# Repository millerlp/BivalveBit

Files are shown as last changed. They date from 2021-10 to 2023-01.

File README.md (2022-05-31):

# BivalveBit

A custom data logger designed to monitor bivalve mollusc heart rate, valve
gape, and external temperature. Designed to be housed in a 3/4" schedule 40 
PVC plumbing pipe along with an 18650-size Lithium-Ion battery cell. 

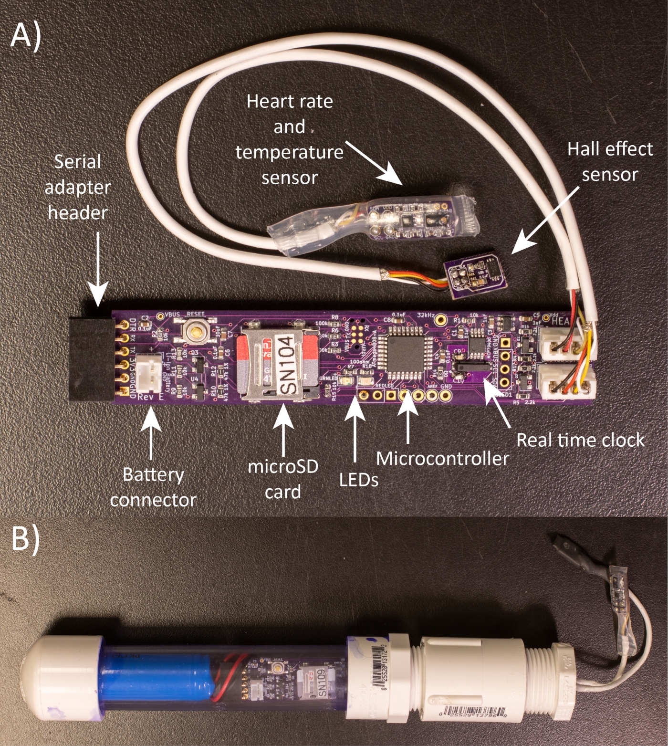
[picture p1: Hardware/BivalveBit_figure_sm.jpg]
Revision E circuit board


Current hardware revision E (Fall 2021). See the Hardware folder for KiCad
design files.

Programmed in the Arduino environment.
 
Requires the separate BivalveBit_lib library available at: 
https://github.com/millerlp/BivalveBit_lib

 Based on ATmega4808 MCU using MegaCoreX board definition
 https://github.com/MCUdude/MegaCoreX

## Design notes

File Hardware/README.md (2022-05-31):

# BivalveBit hardware
 Heart rate and valve gape sensor wearable for oysters and mussels. 
 
 * Based around a ATmega4808 microcontroller
 * Designed to fit inside a nominal 3/4" schedule 40 PVC plumbing pipe (<18.5mm
 inside diameter) along with an 18650 size Lithium-Ion battery cell. 
 * Provides one I2C 4-pin port for communicating with a IR heart rate sensor
 * Provides one analog 4-pin port for communicating with an analog sensor such
 as the A1395 Hall effect sensor (with SLEEP pin on the 4th wire). 
 * Writes data to a standard microSD card
 
 Hardware design files for the main board were originally created in KiCad 5.1, 
 in the directory BivalveBit_RevE. The files have been updated to KiCad 6.0.1. 
 
 Hardware design files for the heart rate (and temperature) sensor board
 were created in Autodesk EAGLE 9.6, and are available in the 
 Mussel_heartrate_RevC_EAGLE directory. A version imported into KiCad 6.0.1 is available
 in the directory Mussel_heartrate_RevC_KiCad. 
 
 Hardware design files in KiCad 6.0.1 for the Hall effect sensor board using an Allegro A1395
 Hall effect sensor can be found in the directory Hall_effect_sensor_board_A139x.

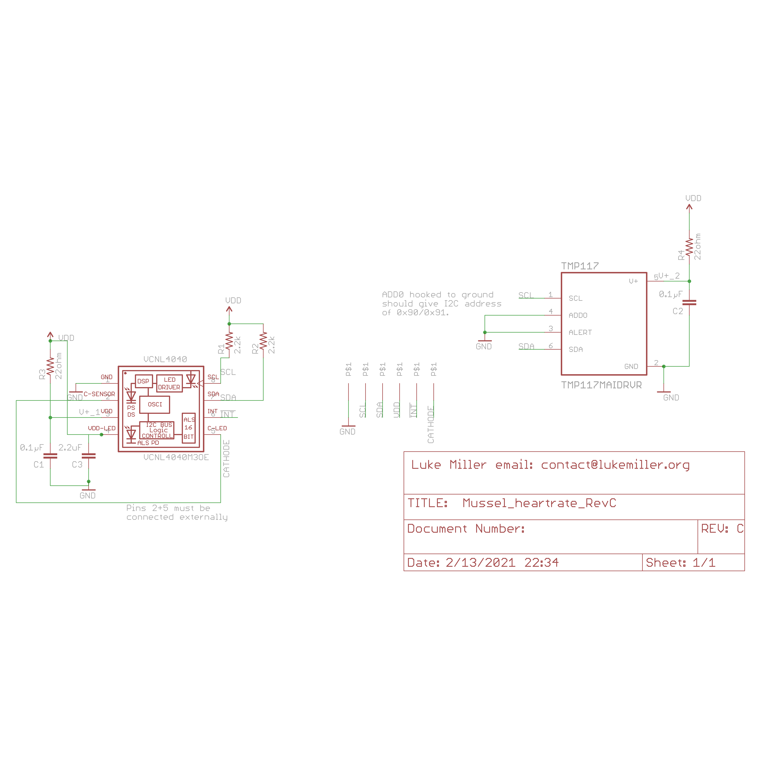
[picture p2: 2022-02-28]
Hardware/Mussel_heartrate_RevC_EAGLE/Mussel_heartrate_RevC_schematic.png

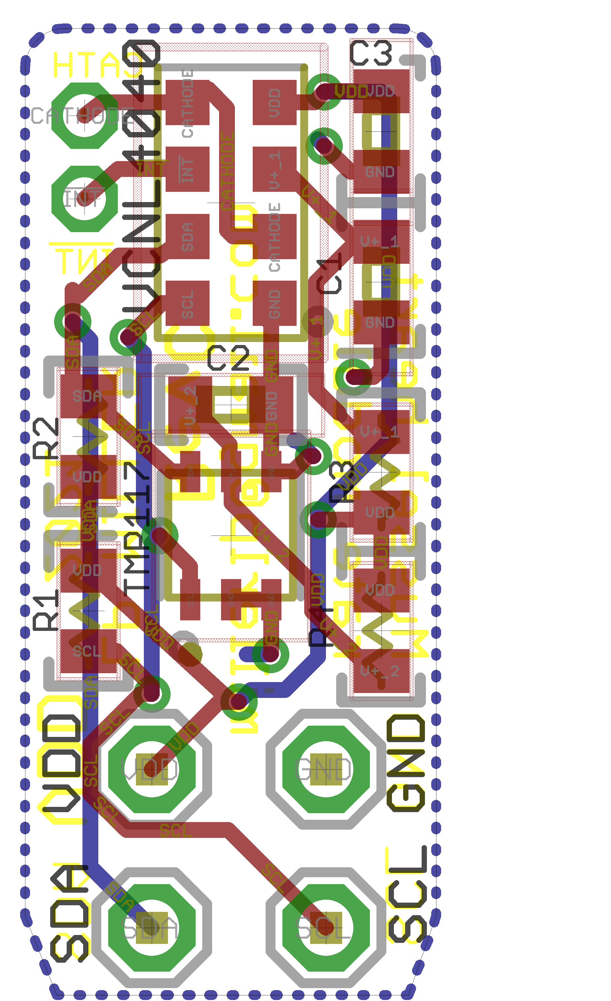
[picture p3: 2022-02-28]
Hardware/Mussel_heartrate_RevC_EAGLE/Mussel_heartrate_RevC_board.png

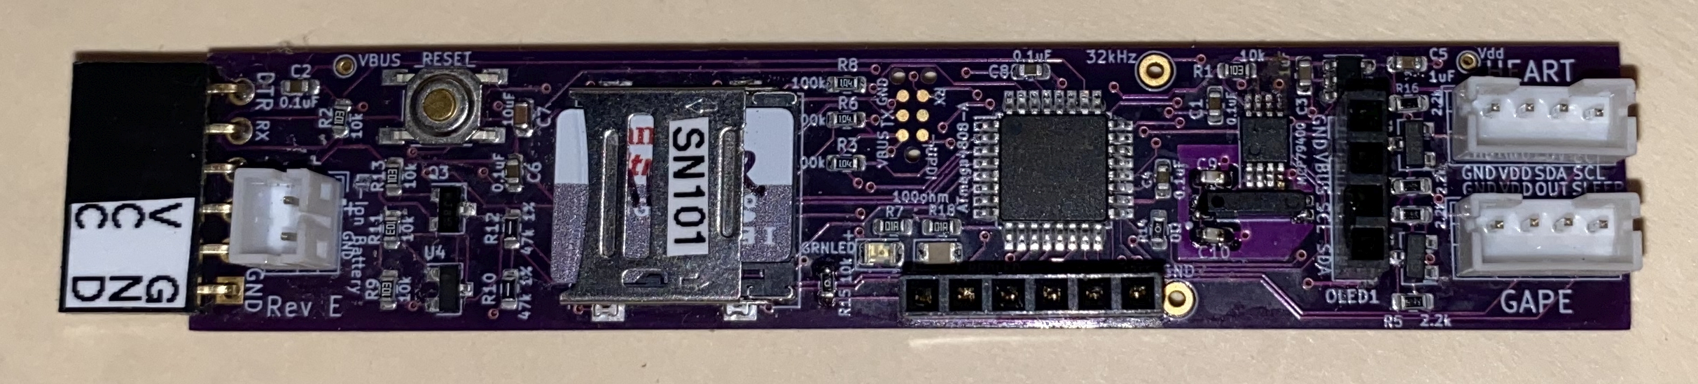
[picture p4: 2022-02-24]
Hardware/BivalveBit_RevE/BivalveBit_RevE_board.jpg

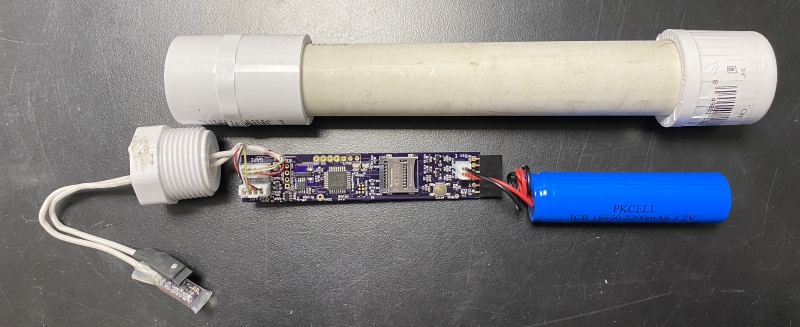
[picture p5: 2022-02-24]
Hardware/BivalveBit_RevE_hardware.jpg

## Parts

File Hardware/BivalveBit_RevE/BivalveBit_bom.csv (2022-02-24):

Id | Designator | Package | Quantity | Designation | Supplier and ref
1 | TP2,TP1 | TestPoint_THTPad_D1.0mm_Drill0.5mm | 2 | TestPoint_Probe
2 | RTC_BATT1 | BatteryHolder_Keystone_3000_1x12mm | 1 | Battery_Cell
3 | JP2,JP1 | SolderJumper-3_P1.3mm_Bridged12_RoundedPad1.0x1.5mm | 2 | SolderJumper_3_Bridged12
4 | HEART_SENSOR1,HALL_SENSOR1 | JST_PH_B4B-PH-K_1x04_P2.00mm_Vertical | 2 | Conn_01x04_Male
5 | R17,R16,R5,R4 | R_0603_1608Metric | 4 | 2.2k
6 | U4 | SOT-23 | 1 | BJT_NPN
7 | U3 | SOT-23-5 | 1 | LP5907MFX-3.0
8 | U2 | TQFP-32_7x7mm_P0.8mm | 1 | ATmega4808-A
9 | SW2 | SW_SPST_REED_CT10-XXXX-G1 | 1 | SW_Reed
10 | RESET1 | SW_PTS525SM15SMTR2LFS | 1 | PTS525SM15SMTR2LFS
11 | R15,R13,R11,R9,R2,R1 | R_0603_1608Metric | 6 | 10k
12 | R14 | R_0603_1608Metric | 1 | 0Ω
13 | R12,R10 | R_0603_1608Metric | 2 | 47k 1%
14 | R8,R6,R3 | R_0603_1608Metric | 3 | 100k
15 | R7,R18 | R_0603_1608Metric | 2 | 100ohm
16 | Q3 | SOT-23 | 1 | P-FET
17 | Q2,Q1 | SOT-23 | 2 | BSS138
18 | PROGRAM_HEADER1 | Tag-Connect_TC2030-IDC-NL_2x03_P1.27mm_Vertical | 1 | TC2030-IDC-NL-UPDI
19 | PRIMARY_BATTERY1 | JST_PH_B2B-PH-K_1x02_P2.00mm_Vertical | 1 | Conn_01x02
20 | OLED1 | PinHeader_1x04_P2.54mm_Vertical | 1 | Conn_01x04
21 | microSD1 | MOLEX_47219-2001 | 1 | 47219-2001
22 | J7,J5,J4,J8,J2 | Pin_D1.0mm_L10.0mm | 5 | Conn_01x01_Male
23 | J6 | PinHeader_1x03_P2.54mm_Vertical | 1 | Conn_01x03_Male
24 | FTDI1 | PinSocket_1x06_P2.54mm_Horizontal | 1 | Conn_01x06
25 | D1 | LED_0805_2012Metric | 1 | GRNLED
26 | Crystal_32.768kHz1 | OSC_SSP-T7-F | 1 | SSP-T7-F
27 | C8,C6,C4,C2,C1 | C_0603_1608Metric | 5 | 0.1uF
28 | C7 | C_0603_1608Metric | 1 | 10uF
29 | C5,C3 | C_0603_1608Metric | 2 | 1uF
30 | C9,C10 | C_0603_1608Metric | 2 | 4-16pF
31 | RTC1 | MSOP-8_3x3mm_P0.65mm | 1 | MCP79400
32 | D2 | LED_0805_2012Metric | 1 | REDLED

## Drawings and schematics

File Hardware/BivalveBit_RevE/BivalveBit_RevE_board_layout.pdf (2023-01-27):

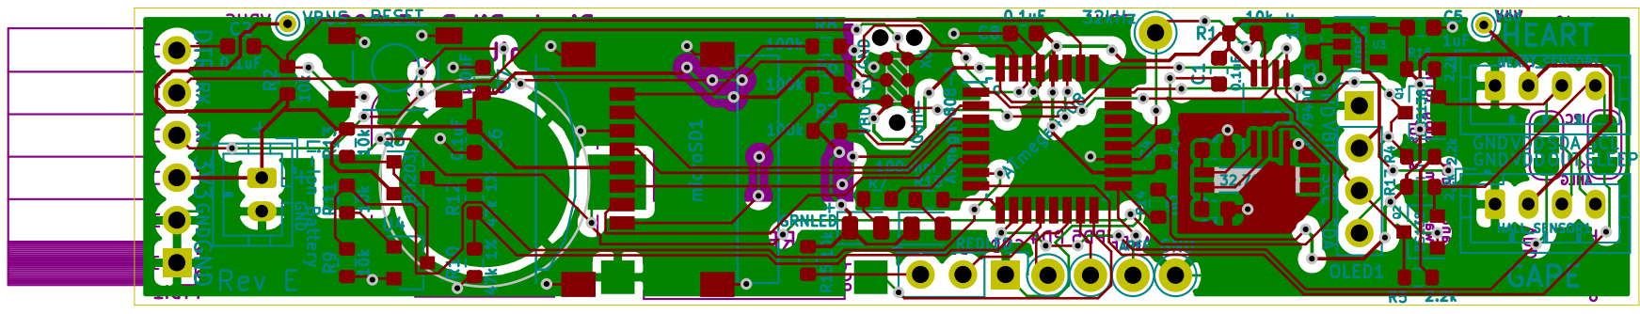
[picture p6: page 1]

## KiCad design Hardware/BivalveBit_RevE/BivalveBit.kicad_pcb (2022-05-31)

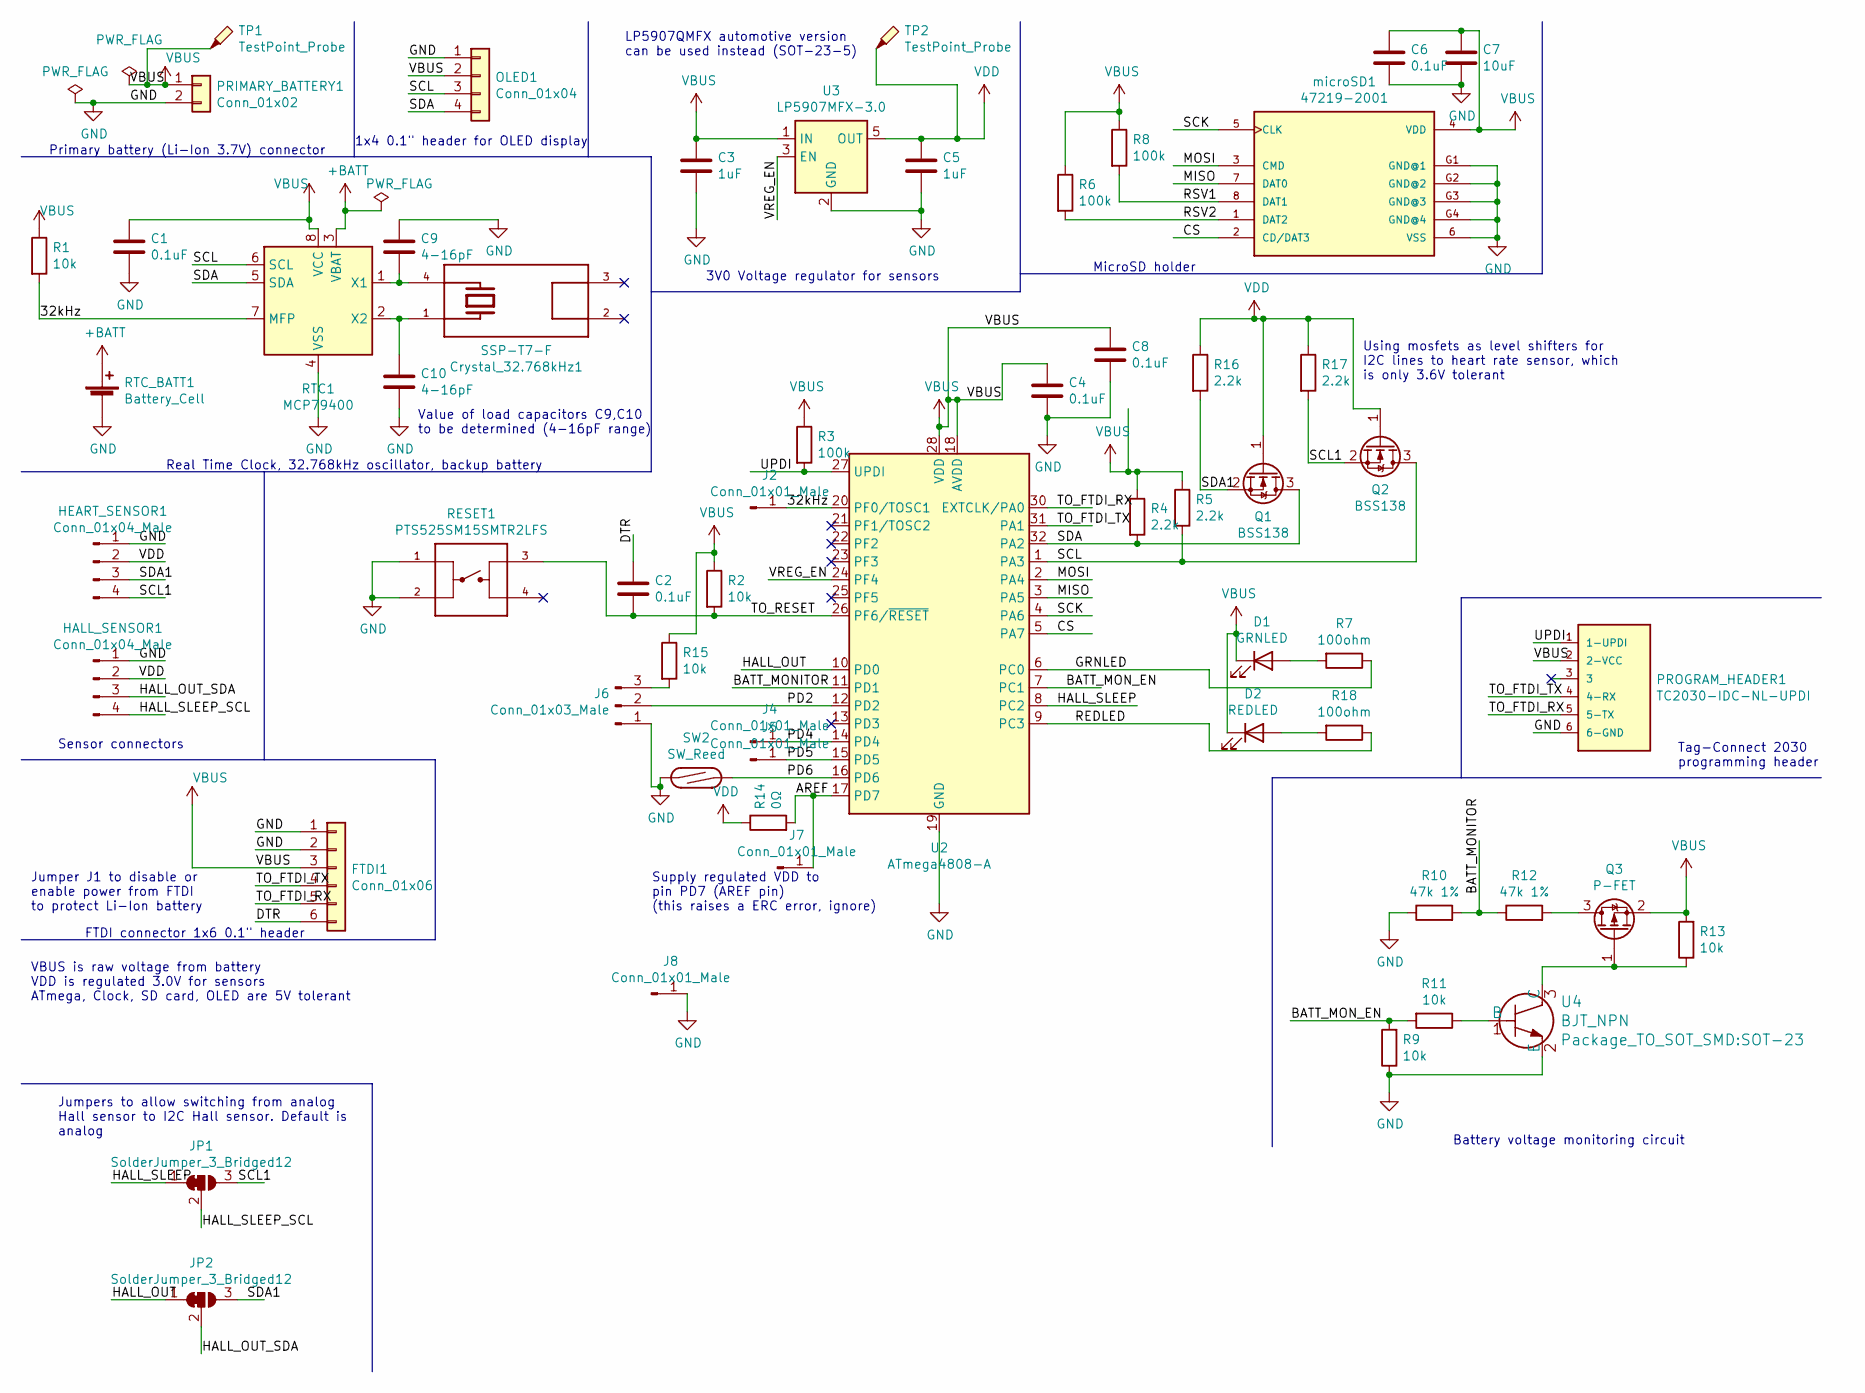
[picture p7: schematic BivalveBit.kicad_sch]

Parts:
C1, C2, C4, C6, C8: 0.1uF; C_0603_1608Metric
C3, C5: 1uF; C_0603_1608Metric
C7: 10uF; C_0603_1608Metric
C9, C10: 4-16pF; C_0603_1608Metric
Crystal_32.768kHz1: SSP-T7-F; OSC_SSP-T7-F; PARTREV N/A
D1: GRNLED; LED_0805_2012Metric
D2: REDLED; LED_0805_2012Metric
FTDI1: Conn_01x06; PinSocket_1x06_P2.54mm_Horizontal
HALL_SENSOR1: Conn_01x04_Male; JST_PH_B4B-PH-K_1x04_P2.00mm_Vertical
HEART_SENSOR1: Conn_01x04_Male; JST_PH_B4B-PH-K_1x04_P2.00mm_Vertical
J2, J4, J5, J7, J8: Conn_01x01_Male; Pin_D1.0mm_L10.0mm
J6: Conn_01x03_Male; PinHeader_1x03_P2.54mm_Vertical
JP1, JP2: SolderJumper_3_Bridged12; SolderJumper-3_P1.3mm_Bridged12_RoundedPad1.0x1.5mm
OLED1: Conn_01x04; PinHeader_1x04_P2.54mm_Vertical
PRIMARY_BATTERY1: Conn_01x02; JST_PH_B2B-PH-K_1x02_P2.00mm_Vertical
PROGRAM_HEADER1: TC2030-IDC-NL-UPDI; Tag-Connect_TC2030-IDC-NL_2x03_P1.27mm_Vertical; PARTREV MS
Q1, Q2: BSS138; SOT-23
Q3: P-FET; SOT-23
R1, R2, R9, R11, R13, R15: 10k; R_0603_1608Metric
R3, R6, R8: 100k; R_0603_1608Metric
R4, R5, R16, R17: 2.2k; R_0603_1608Metric
R7, R18: 100ohm; R_0603_1608Metric
R10, R12: 47k 1%; R_0603_1608Metric
R14: 0Ω; R_0603_1608Metric
RESET1: PTS525SM15SMTR2LFS; SW_PTS525SM15SMTR2LFS; PARTREV NA
RTC1: MCP79400; MSOP-8_3x3mm_P0.65mm
RTC_BATT1: Battery_Cell; BatteryHolder_Keystone_3000_1x12mm
SW2: SW_Reed; SW_SPST_REED_CT10-XXXX-G1
TP1, TP2: TestPoint_Probe; TestPoint_THTPad_D1.0mm_Drill0.5mm
U2: ATmega4808-A; TQFP-32_7x7mm_P0.8mm
U3: LP5907MFX-3.0; SOT-23-5
U4: BJT_NPN; SOT-23
microSD1: 47219-2001; MOLEX_47219-2001; Digikey WM6698CT-ND

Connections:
+BATT: RTC1.3 (VBAT), RTC_BATT1.1 (+)
/32kHz: J2.1, R1.2, RTC1.7 (MFP), U2.20 (PF0/TOSC1)
/AREF: J7.1, R14.2, U2.17 (PD7)
/BATT_MONITOR: R10.2, R12.1, U2.11 (PD1)
/BATT_MON_EN: R9.2, R11.2, U2.7 (PC1)
/CS: U2.5 (PA7), microSD1.2 (CD/DAT3)
/DTR: C2.1, FTDI1.6
/GRNLED: R7.1, U2.6 (PC0)
/HALL_OUT: JP2.1 (A), U2.10 (PD0)
/HALL_OUT_SDA: HALL_SENSOR1.3, JP2.2 (C)
/HALL_SLEEP: JP1.1 (A), U2.8 (PC2)
/HALL_SLEEP_SCL: HALL_SENSOR1.4, JP1.2 (C)
/MISO: U2.3 (PA5), microSD1.7 (DAT0)
/MOSI: U2.2 (PA4), microSD1.3 (CMD)
/PD2: J6.2, U2.12 (PD2)
/PD4: J4.1, U2.14 (PD4)
/PD5: J5.1, U2.15 (PD5)
/PD6: SW2.2, U2.16 (PD6)
/REDLED: R18.1, U2.9 (PC3)
/RSV1: R8.2, microSD1.8 (DAT1)
/RSV2: R6.2, microSD1.1 (DAT2)
/SCK: U2.4 (PA6), microSD1.5 (CLK)
/SCL: OLED1.3, Q2.3 (D), R5.2, RTC1.6 (SCL), U2.1 (PA3)
/SCL1: HEART_SENSOR1.4, JP1.3 (B), Q2.2 (S), R17.2
/SDA: OLED1.4, Q1.3 (D), R4.2, RTC1.5 (SDA), U2.32 (PA2)
/SDA1: HEART_SENSOR1.3, JP2.3 (B), Q1.2 (S), R16.2
/TO_FTDI_RX: FTDI1.5, PROGRAM_HEADER1.5 (5-TX), U2.30 (EXTCLK/PA0)
/TO_FTDI_TX: FTDI1.4, PROGRAM_HEADER1.4 (4-RX), U2.31 (PA1)
/TO_RESET: C2.2, R2.2, RESET1.3, U2.26 (PF6/~RESET)
/UPDI: PROGRAM_HEADER1.1 (1-UPDI), R3.2, U2.27 (UPDI)
/VREG_EN: U2.24 (PF4), U3.3 (EN)
GND: C1.2, C3.2, C4.2, C5.2, C6.2, C7.2, C8.2, C9.1, C10.2, FTDI1.1, FTDI1.2, HALL_SENSOR1.1, HEART_SENSOR1.1, J6.1, J8.1, OLED1.1, PRIMARY_BATTERY1.2, PROGRAM_HEADER1.6 (6-GND), R9.1, R10.1, RESET1.1, RESET1.2, RTC1.4 (VSS), RTC_BATT1.2 (-), SW2.1, U2.19 (GND), U2.29 (GND), U3.2 (GND), U4.2 (E), microSD1.6 (VSS), microSD1.G1 (GND@1), microSD1.G2 (GND@2), microSD1.G3 (GND@3), microSD1.G4 (GND@4)
unnamed: C9.2, Crystal_32.768kHz1.4, RTC1.1 (X1)
unnamed: C10.1, Crystal_32.768kHz1.1, RTC1.2 (X2)
unnamed: D1.2 (A), R7.2
unnamed: D2.2 (A), R18.2
unnamed: J6.3, R15.2
unnamed: Q3.1 (G), R13.1, U4.3 (C)
unnamed: Q3.3 (D), R12.2
unnamed: R11.1, U4.1 (B)
VBUS: C1.1, C3.1, C4.1, C6.1, C7.1, C8.1, D1.1 (K), D2.1 (K), FTDI1.3, OLED1.2, PRIMARY_BATTERY1.1, PROGRAM_HEADER1.2 (2-VCC), Q3.2 (S), R1.1, R2.1, R3.1, R4.1, R5.1, R6.1, R8.1, R13.2, R15.1, RTC1.8 (VCC), TP1.1, U2.18 (AVDD), U2.28 (VDD), U3.1 (IN), microSD1.4 (VDD)
VDD: C5.1, HALL_SENSOR1.2, HEART_SENSOR1.2, Q1.1 (G), Q2.1 (G), R14.1, R16.1, R17.1, TP2.1, U3.5 (OUT)

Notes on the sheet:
Primary battery (Li-Ion 3.7V) connector
Battery voltage monitoring circuit
Using mosfets as level shifters for I2C lines to heart rate sensor, which is only 3.6V tolerant
Jumpers to allow switching from analog Hall sensor to I2C Hall sensor. Default is analog
FTDI connector 1x6 0.1" header
Sensor connectors
1x4 0.1" header for OLED display
Real Time Clock, 32.768kHz oscillator, backup battery
Supply regulated VDD to pin PD7 (AREF pin) (this raises a ERC error, ignore)
Value of load capacitors C9,C10 to be determined (4-16pF range)
LP5907QMFX automotive version can be used instead (SOT-23-5)
Jumper J1 to disable or enable power from FTDI to protect Li-Ion battery
3V0 Voltage regulator for sensors
VBUS is raw voltage from battery VDD is regulated 3.0V for sensors ATmega, Clock, SD card, OLED are 5V tolerant
MicroSD holder
Tag-Connect 2030 programming header

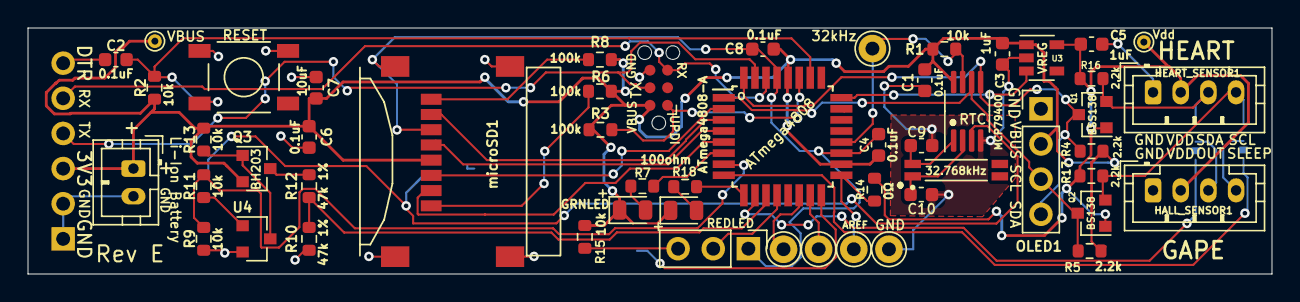
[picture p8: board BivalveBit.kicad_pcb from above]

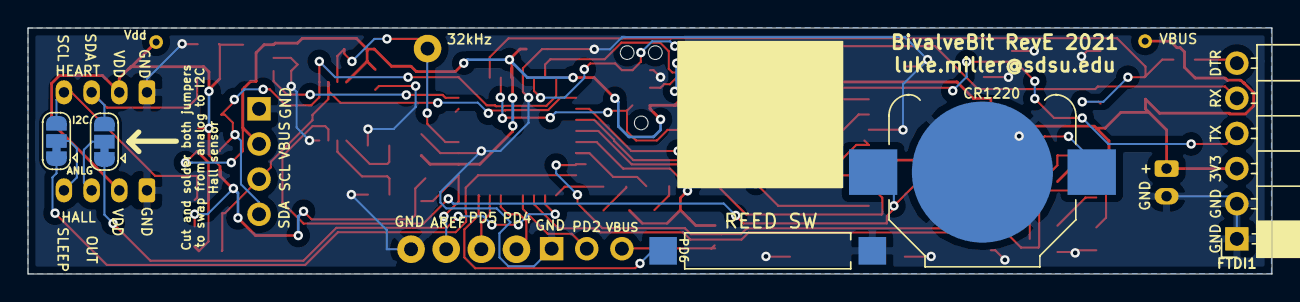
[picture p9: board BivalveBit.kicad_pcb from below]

Board: 2 copper layers, 89.9 x 17.8 mm, 58 parts (5 on the bottom side), 42 nets.

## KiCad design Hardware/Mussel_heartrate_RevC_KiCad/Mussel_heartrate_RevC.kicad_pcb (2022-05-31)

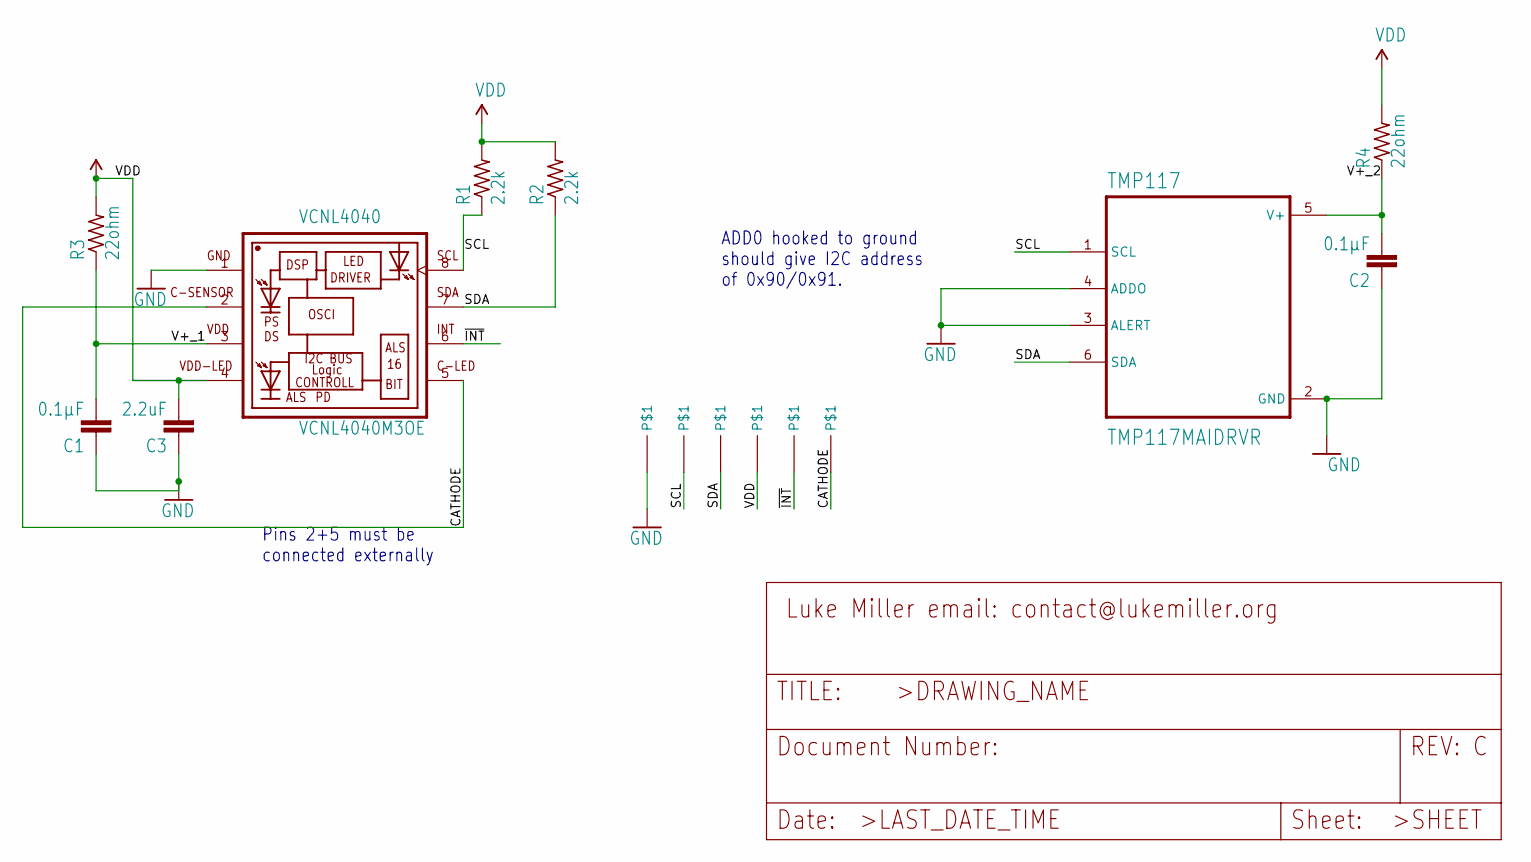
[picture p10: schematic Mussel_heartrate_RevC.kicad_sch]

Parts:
/~{INT}1: PINHD-1X10.7MM_DRILL; 1X01_SMALL_0.7
C1, C2: 0.1µF; C0402
C3: 2.2uF; C0402
CATHODE1: PINHD-1X10.7MM_DRILL; 1X01_SMALL_0.7
GND1: PINHD-1X1SMALL; 1X01_SMALL_HEADER_PIN_D0.9MM_W1.4MM
R1, R2: 2.2k; R0402
R3, R4: 22ohm; R0402
SCL1: PINHD-1X1SMALL; 1X01_SMALL_HEADER_PIN_D0.9MM_W1.4MM
SDA1: PINHD-1X1SMALL; 1X01_SMALL_HEADER_PIN_D0.9MM_W1.4MM
TMP117: TMP117MAIDRVR; SON65P200X200X80-7N
VCNL4040: VCNL4040M3OE; VISHAY_VCNL4040_4X2X1.1
VDD1: PINHD-1X1SMALL; 1X01_SMALL_HEADER_PIN_D0.9MM_W1.4MM

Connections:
/CATHODE: CATHODE1.P$1, VCNL4040.2 (C-SENSOR), VCNL4040.5 (C-LED)
/SCL: R1.1, SCL1.1, TMP117.1 (SCL), VCNL4040.8 (SCL)
/SDA: R2.1, SDA1.1, TMP117.6 (SDA), VCNL4040.7 (SDA)
/V+_1: C1.2, R3.1, VCNL4040.3 (VDD)
/V+_2: C2.2, R4.1, TMP117.5 (V+)
/~INT: /~{INT}1.P$1, VCNL4040.6 (INT)
GND: C1.1, C2.1, C3.1, GND1.1, TMP117.2 (GND), TMP117.3 (ALERT), TMP117.4 (ADDO), VCNL4040.1 (GND)
VCC: C3.2, R1.2, R2.2, R3.2, R4.2, VCNL4040.4 (VDD-LED), VDD1.1

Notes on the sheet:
ADD0 hooked to ground should give I2C address of 0x90/0x91.
Pins 2+5 must be connected externally

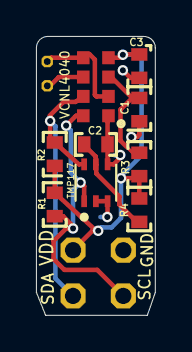
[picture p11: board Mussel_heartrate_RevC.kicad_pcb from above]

Board: 2 copper layers, 6.6 x 15.5 mm, 15 parts (0 on the bottom side), 8 nets.

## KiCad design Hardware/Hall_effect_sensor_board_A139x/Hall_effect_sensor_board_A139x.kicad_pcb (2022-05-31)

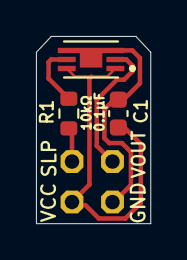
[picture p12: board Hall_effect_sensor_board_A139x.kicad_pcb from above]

Board: 2 copper layers, 6.4 x 10.4 mm, 4 parts (0 on the bottom side), 5 nets.

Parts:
C1: 0.1µF; C_0603_1608Metric
HALL1_HEADER1: PINHD-2X21.5MM_SILK; 2X2_2.25MM
R1: 10kΩ; R_0603_1608Metric
U1: A1395SEHLT-T; SENSOR_A1395SEHLT-T

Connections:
/HALL1_GND: C1.2, HALL1_HEADER1.P$1 (1), U1.3 (GND), U1.4 (GND)
/HALL1_VCC: C1.1, HALL1_HEADER1.P$2 (2), U1.1 (VCC), U1.6 (VREF)
/HALL1_VOUT: HALL1_HEADER1.P$3 (3), U1.2 (OUT)
/HALL1_~SLEEP_IN: HALL1_HEADER1.P$4 (4), R1.1
/~SLEEP1: R1.2, U1.5 (~SLEEP)

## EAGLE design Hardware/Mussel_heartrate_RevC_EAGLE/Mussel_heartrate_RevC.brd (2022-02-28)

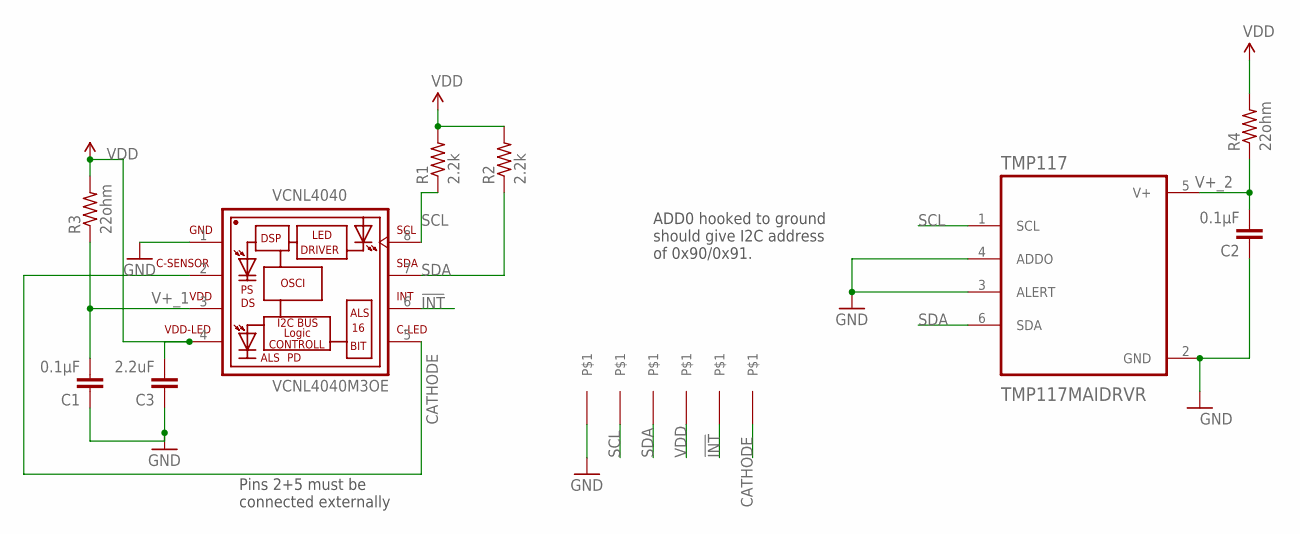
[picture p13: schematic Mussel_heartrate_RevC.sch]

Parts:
!INT, !INT1: PINHD-1X10.7MM_DRILL; 1X01_SMALL_0.7
C1, C2: 0.1µF; C0402
C3: 2.2uF; C0402
GND: PINHD-1X1SMALL; 1X01_SMALL
R1, R2: 2.2k; R0402
R3, R4: 22ohm; R0402
SCL: PINHD-1X1SMALL; 1X01_SMALL
SDA: PINHD-1X1SMALL; 1X01_SMALL
TMP117: TMP117MAIDRVR; SON65P200X200X80-7N
VCNL4040: VCNL4040M3OE; VISHAY_VCNL4040_4X2X1.1
VDD: PINHD-1X1SMALL; 1X01_SMALL

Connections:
!INT: !INT.P$1, VCNL4040.6 (INT)
CATHODE: !INT1.P$1, VCNL4040.2 (C-SENSOR), VCNL4040.5 (C-LED)
GND: C1.1, C2.1, C3.1, GND.1, TMP117.2 (GND), TMP117.3 (ALERT), TMP117.4 (ADDO), VCNL4040.1 (GND)
SCL: R1.1, SCL.1, TMP117.1 (SCL), VCNL4040.8 (SCL)
SDA: R2.1, SDA.1, TMP117.6 (SDA), VCNL4040.7 (SDA)
V+_1: C1.2, R3.1, VCNL4040.3 (VDD)
V+_2: C2.2, R4.1, TMP117.5 (V+)
VDD: C3.2, R1.2, R2.2, R3.2, R4.2, VCNL4040.4 (VDD-LED), VDD.1

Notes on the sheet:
ADD0 hooked to ground should give I2C address of 0x90/0x91.
Pins 2+5 must be connected externally

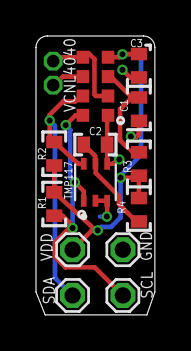
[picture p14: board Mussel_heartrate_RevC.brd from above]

Board: 2 copper layers, 6.6 x 15.5 mm, 15 parts (0 on the bottom side), 8 nets.

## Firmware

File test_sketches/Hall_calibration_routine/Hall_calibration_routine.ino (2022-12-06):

/* Hall_calibration_routine.ino
 *  BivalveBit data logger program to calibration Hall effect sensor
 *  of a KD Scientific Model 200 syringe dispenser.
 *  
 *  Compile with MegaCoreX: ATmega4808, 32 pin, BOD 2.6V, Internal 8MHz, Optiboot (UART0 default pins)
 *  

 *  Meant to work with a BivalveBit board. Connect
 *  to a KD Scientific Model 200 syringe dispenser to move the 
 *  dispenser a known distances, causing the 
 *  magnetic field of a Hall effect sensor to change in response.
 *  If you don't have a Model 200 syringe dispenser sitting around,
 *  don't bother running this program.
 *  
 *  Connect Syringe Trigger pin to MusselTracker pin PD2
 *  Connect Syringe GND to MusselTracker GND
 *  On the KD200 dispenser, set the syringe DIA to 50.00mm
 *  Set the Vol to 0.623ml
 *  Set the Rate to 40 ml/m
 *  
 *  To start a calibration run, open the Serial Monitor and type CALIB and 
 *  hit return. The program will step the syringe pump through the various 
 *  distances, with the first distance marked as "0.0" mm. It will stop after 
 *  moving about 12mm, at which point you can release the carriage and return
 *  it to a starting point. Another run can be started by typing CALIB again,
 *  and the new run will written into the same file as the previous run. 
 *  
 *  If the device just slowly flashes red after startup, the real time clock
 *  needs to be reset. Open the serial monitor and enter the correct date and
 *  time (in the UTC time zone preferably) using the command format:
 *  SETDATE YYYY-MM-DD HH:MM:SS
 *  
 */


#include "SdFat.h" // https://github.com/greiman/SdFat (you must be using ver. 2.1.2 or higher)
#include <Wire.h>  // built in library, for I2C communications
#include <EEPROM.h>
#include <avr/io.h>
#include <avr/interrupt.h>
#include <avr/sleep.h>
#include <avr/cpufunc.h>
//#include "SSD1306Ascii.h" // https://github.com/greiman/SSD1306Ascii
//#include "SSD1306AsciiWire.h" // https://github.com/greiman/SSD1306Ascii
#include "MCP7940.h"  // https://github.com/Zanduino/MCP7940  Real time clock
//#include "Adafruit_VCNL4040.h" // https://github.com/adafruit/Adafruit_VCNL4040 & https://github.com/adafruit/Adafruit_BusIO
//#include "SparkFun_TMP117.h" // https://github.com/sparkfun/SparkFun_TMP117_Arduino_Library
#include "BivalveBit_lib.h" // https://github.com/millerlp/BivalveBit_lib


//*************************************
float moveDist = 0.3175; // units mm, if pump set to dispense 0.1mL
float moveLimit = 12.5; // units millimeters
float distanceVal = 0; // keep track of distance moved
uint8_t TrialNum = 0;   // Trial number counter
//*************

// -------------------------------------------
// ***** STATE MACHINE TYPE DEFINITIONS *****
typedef enum STATE
{
  STATE_IDLE,         // Idle and wait for user input
  STATE_CALIB     // Go into Hall effect calibration mode
} mainState_t;
// main state machine variable, this takes on the various
// values defined for the STATE typedef above. 
mainState_t mainState;

// Type definition for a case structure to write to SD card or skip writing
typedef enum WRITE_SD
{
  WRITE_HALL_TEMP_VOLTS, // collect Hall sensor data and battery voltage data
  WRITE_HEART, // collect heart rate data at sub-second intervals
  WRITE_NOTHING // don't write anything
  
} writeState_t;
writeState_t writeState;

/*******************************************************
 * SD card objects
 *******************************************************/
// SPI pins for SD card
const uint8_t SD_CHIP_SELECT = 7;
#define MOSI 4
#define MISO 5
#define SCK 6
SdFat sd; 
SdFile GAPEFile; //SD card object
bool SDfailFlag = false;
// Placeholder serialNumber
char serialNumber[] = "SN000";
bool serialValid = false;
// Declare initial name for output files written to SD card
char gapefilename[] =   "SN000_YYYYMMDD_HHMM_CALIB.csv";

/************************************************************
 * Hall effect sensor definitions
 ************************************************************/
#define ANALOG_IN A0  // Analog input pin for Hall sensor
#define HALL_SLEEP 10 // Hall sensor sleep pin, pull high to wake
unsigned int HallValue = 0; // Variable for Hall sensor reading

/***************************************************************************************************
** Declare global variables and instantiate classes for MCP79400 real time clock                                              
*   This library is written for the MCP7940, but works with the BivalveBit MCP79400
***************************************************************************************************/
MCP7940_Class MCP7940;                           // Create an instance of the MCP7940

const uint32_t SERIAL_SPEED{57600};     // Set the baud rate for Serial I/O
const uint8_t  SPRINTF_BUFFER_SIZE{32};  // Buffer size for sprintf()
char          inputBuffer[SPRINTF_BUFFER_SIZE];  // Buffer for sprintf()/sscanf()
DateTime now; // Variable to hold current time
DateTime firsttimestamp; // Variable to track fast sampling start 
DateTime lasttimestamp; // Variable to track fast sampling end time
byte oldday1; // Used to track midnight change
byte oldday2; // Used to track midnight change
/*! ///< Enumeration of MCP7940 alarm types */
enum alarmTypes {
  matchSeconds,
  matchMinutes,
  matchHours,
  matchDayOfWeek,
  matchDayOfMonth,
  Unused1,
  Unused2,
  matchAll,
  Unknown
};

//------------------------------------------------------------
//  Battery monitor 
#define BATT_MONITOR_EN  9 // digital output channel to turn on battery voltage check
#define BATT_MONITOR  A1  // analog input channel to sense battery voltage
float dividerRatio = 2; // Ratio of voltage divider (47k + 47k) / 47k = 2
float refVoltage = 3.00; // Voltage at AREF pin on ATmega microcontroller, measured per board
float batteryVolts = 0; // Estimated battery voltage returned from readBatteryVoltage function
float minimumVoltage = 3.4; // Minimum safe voltage for a Li-Ion battery
unsigned int lowVoltageCount = 0; // Count how many times voltage is too low
unsigned int lowVoltageCountLimit = 10; // Number of loops after which the program should be shutdown
#define REDLED 11   // Red LED pin
#define GRNLED 8    // Green LED pin
#define VREG_EN 24  // voltage regulator enable
#define TRIGGER 14 // External trigger to syringe pump, PD2 pin, Arduino pin 14(A2)


void test_pin_init(void){
    /* Make High (OFF) */
    PORTC.OUT |= PIN0_bm; // BivalveBit green led on pin PC0 (arduino pin 8)
    /* Make output */
    PORTC.DIR |= PIN0_bm;

    /* Make High (OFF) */
    PORTC.OUT |= PIN3_bm; // BivalveBit red led on pin PC3 (arduino pin 11)
    /* Make output */
    PORTC.DIR |= PIN3_bm;
    
    /* Make High (OFF) */
    PORTD.OUT |= PIN2_bm; // Pin PD2 (probe with scope/analyzer) - used to activate syringe pump
    /* Make output */
    PORTD.DIR |= PIN2_bm;
}

ISR(RTC_PIT_vect)
{
    /* You must clear PIT interrupt flag by writing '1': */
    RTC.PITINTFLAGS = RTC_PI_bm;
//    PORTD.OUTTGL |= PIN2_bm; // Toggle PD2 (probe with scope/analyzer)
//    PORTC.OUTTGL |= PIN0_bm; // BivalveBit green led on pin PC0 
}



//---------------------------------------------------------------
//-------- Setup
//---------------------------------------------------------------
void setup() {
  Serial.begin(57600);
  Serial.println("Hello");
  analogReference(EXTERNAL);
  setUnusedPins(); // in BivalveBit_lib
  disableUnusedPeripherals(); // in BivalveBit_lib
  pinMode(VREG_EN, OUTPUT);   // Voltage regulator pin
  digitalWrite(VREG_EN, LOW); // set low to turn off, high to turn on (~150usec to wake)
  pinMode(20, INPUT_PULLUP); // pin PF0, attached to RTC multi-function pin
  // Battery monitor pins
  pinMode(BATT_MONITOR, INPUT); // Battery voltage input channel
  pinMode(BATT_MONITOR_EN, OUTPUT); // Battery monitor enable pin
  digitalWrite(BATT_MONITOR_EN, LOW); // pull low to turn off battery monitor circuit
  test_pin_init(); // Set up the LEDs and PD2 output pin
  //---------------------------------
  // Retrieve board serial number
  EEPROM.get(0, serialNumber);
  if (serialNumber[0] == 'S') {
    serialValid = true; // set flag   
    Serial.print("Serial number: "); Serial.println(serialNumber); 
  } else {
    serialValid = false;
    Serial.print("No serial number");
  }
  //----------------------------------------------------------
  // SD card initialization
  pinMode(SD_CHIP_SELECT, OUTPUT); // SD card chip select pin
  if (!sd.begin(SD_CHIP_SELECT)) {
    Serial.println("Card failed, or not present");
    SDfailFlag = true;
    for (int i = 0; i < 50; i++){
      digitalWrite(REDLED, !digitalRead(REDLED));
      delay(100);
      digitalWrite(GRNLED, !digitalRead(GRNLED));
      delay(100);
    }
    return;
  } else {
    Serial.println("SD Card initialized.");
  }
  digitalWrite(GRNLED,LOW); // set low to turn on
  delay(500);
  digitalWrite(GRNLED,HIGH); // set high to turn off
  //---------------------------------------------------------------
  digitalWrite(VREG_EN, HIGH); // set low to turn off, high to turn on (~150usec to wake)

  //--------------------------------------------------------------
  MCP7940setup();
  // Turn on battery backup, default is off
  MCP7940.setBattery(true); // enable battery backup mode
  Serial.print("Battery Backup mode is ");
  if (MCP7940.getBattery()) {
   Serial.println("enabled.");
  } else {
   Serial.println("disabled.");
  }
  now = MCP7940.now();  // get the current time
  // Use sprintf() to pretty print date/time with leading zeroes
  sprintf(inputBuffer, "%04d-%02d-%02d %02d:%02d:%02d", now.year(), now.month(), now.day(),
          now.hour(), now.minute(), now.second());
  Serial.print("Date/Time: "); Serial.println(inputBuffer);
  
  bool clockErrorFlag = true;
  while (clockErrorFlag){
    // Check that real time clock has a reasonable time value
    if ( (now.year() < 2022) | (now.year() > 2035) ) {
        Serial.println("Please set clock to current UTC time");
        Serial.println("Use format SETDATE YYYY-MM-DD HH:MM:SS");
       // Error, clock isn't set
       while(clockErrorFlag){
        digitalWrite(REDLED, !digitalRead(REDLED));
        delay(500);
        readCommand();
        now = MCP7940.now();  // get the updated time
        if ( (now.year() >= 2022) & (now.year() <= 2035) ){
          // If the year is now within bounds, break out of this while statement
          clockErrorFlag = false;
          sprintf(inputBuffer, "%04d-%02d-%02d %02d:%02d:%02d", now.year(), now.month(), now.day(),
            now.hour(), now.minute(), now.second());
          Serial.print("Date/Time: "); Serial.println(inputBuffer);
          break;
        }
        
       }
    } else {
      // If the time's year was in bound, continue with the program
      clockErrorFlag = false;
    }
  }
  oldday1 = oldday2 = now.day(); // Store current day's value
  // Initialize data file
//  initGapeFileName(sd, GAPEFile, now, gapefilename, serialValid, serialNumber);
  digitalWrite(REDLED, HIGH); // turn off
//  Serial.print("Heart sample interval: "); Serial.print(heartMinute); Serial.println(" minutes");
//  MCP7940Alarm1Minute(now); // Set RTC multifunction pin to alarm when new minute hits
  attachInterrupt(digitalPinToInterrupt(20),RTC1MinuteInterrupt, CHANGE); // pin 20 to RTC
  
  mainState = STATE_IDLE;
  writeState = WRITE_NOTHING;
//  SLPCTRL_init(); // in BivalveBitlib - sets up sleep mode
//  sleep_cpu();    // put the cpu to sleep

}     // end setup
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

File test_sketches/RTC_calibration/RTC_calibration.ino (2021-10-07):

/* This assumes you have a 32.768kHz clock signal hooked up
 *  to the RTC pin on the Atmega4808. 
 *  
 *  
 *  Based on code from Microchip bulletin TB3213
 *  http://ww1.microchip.com/downloads/en/AppNotes/TB3213-Getting-Started-with-RTC-90003213A.pdf
 *  
 *  
 *  Set up the RTC on the 4808 to take an external clock signal
 *  which will be the 32.768kHz signal from the separate real time
 *  clock chip. Have it fire an interrupt once per second, which will 
 *  be counted. Also take in a 1 pulse-per-second signal on a digital
 *  pin from a GPS module, firing an interrupt each time.
 *  
 *  After a set number of GPS interrupts has fired, read the count of the 
 *  RTC interrupts that had fired, and read the current
 *  value of the RTC.CNT register to get its value (which should be very 
 *  near another full 1-second tick when the GPS tick happens). 
 *  
 *  
 *  TODO: RTC interrupt counter is running at 1/2 speed (2 seconds)
 */

#include <MCP7940.h>  // https://github.com/Zanduino/MCP7940  Address 0x6F
#include <Wire.h>
#include "SSD1306Ascii.h" // https://github.com/greiman/SSD1306Ascii
#include "SSD1306AsciiWire.h" // https://github.com/greiman/SSD1306Ascii


volatile long RTCticks = 0; // Used to count RTC interrupts
volatile long GPSticks = 0; // Used to count GPSticks
volatile uint16_t rtcRawCount; // Used to count clock cycles on 32.768kHz RTC counter
long oldGPSticks = 0;
uint16_t TimeIntervalSeconds = 30; // Testing interval - use 60 seconds or greater to allow 
                                   // for the clock trimming to be effective
                                   
int8_t trimValue = 0; // Signed crystal frequency trimming value -127 to +127
long oldticks = 0;

#define GPSinput 14 // Take input on PD2, digital pin 14
#define GRNLED 8 

#define RTC_EXAMPLE_PERIOD (32767) // Set how high the RTC will run before overflow (max 32767)

SSD1306AsciiWire oled; // create OLED display object, using I2C Wire1 port
#define I2C_ADDRESS1 0x3C // for OLED. DIY mall units list 0x78 as address, but need 0x3C to work here

MCP7940_Class MCP7940;                           // Create an instance of the MCP7940
const uint8_t  SPRINTF_BUFFER_SIZE{32};  // Buffer size for sprintf()
char          inputBuffer[SPRINTF_BUFFER_SIZE];  // Buffer for sprintf()/sscanf()

void setup() {
  Serial.begin(57600);
  Serial.println("Hello");

  Wire.begin();
  pinMode(GPSinput, INPUT);
  pinMode(GRNLED, OUTPUT);
  digitalWrite(GRNLED, HIGH);
  pinMode(17, OUTPUT);  // PD5 = D17
  pinMode(16, OUTPUT);  // PD4 = D16
  Serial.println("Clock check");
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

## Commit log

2021-08-23 Basic working example, need to calibrate
2021-08-27 Working with TMP117 sensor
2021-08-31 Testing battery voltage reading
2021-09-01 Testing different voltage references
2021-09-01 Minimal working version
    For some reason some of the RevB boards were acting flaky and apparently resetting partway through the setup loop (browning out?), but in other cases they work fine.
2021-09-22 Need to turn on VREG to test sensor
2021-09-22 Give VREG time to turn on
    Before searching for the temp sensor, make sure the VREG has powered up fully (~150 µsec)
2021-09-22 Fix LED pin assignments, turn on VREG
2021-09-28 Building boards 103/104, with 6pF crystal caps
2021-11-01 New unified test program
    Use to test newly assembled sensors
2021-11-01 Making new boards
2021-11-01 Fix printing sd message
2021-11-01 Testing LEDs at start
2022-01-01 Incomplete - working on ISR pin change
    Need to put together ISR and learn how to handle pin change interrupt correctly
2022-01-11 Working wake-from-sleep at 1Hz
2022-01-14 Testing lower powered modes
2022-01-19 Working alarm pin test
2022-01-21 Adding 2 interrupt routines
    1 for 8Hz fast wakes, 1 for 1-minute wakeups. TODO: ensure that the 8Hz PIT disabling routine works.
    TODO: incorporate sensor sampling and SD card writing
2022-01-25 Working test of 8Hz / 1minute timers
    Appears to swap back and forth between the 8Hz fast sampling and 1-minute interval alarms.
2022-01-26 Starting to add in more functions
    Beginning to incorporate sensor objects and getting SD card stuff going. Still need to initialize files and add code to start new files each day.
2022-01-27 Partly working - TODOs
    Need to implement the actual IR sensor reading and writing to buffer.
    Also have an issue with board going into a reset loop when on FTDI power only and no OLED screen attached, probably a voltage droop issue and lack of capacitance in the I2C bus.
2022-01-31 Using this to test settings on IR sensor
2022-01-31 TODO: fix IR sensor readout
    I'm not getting proper readout from the IR sensor right now, possibly it needs more time to awaken and integrate measurement before being read.
2022-02-01 Testing version - start battery tests
    All sensors functional, set to sample heart every other minute for 30 seconds at 8Hz.
2022-02-24 KiCad files
    [BivalveBit.kicad_pcb, BivalveBit.sch, BivalveBit_RevE_BOM.xlsx, BivalveBit_bom.csv]
2022-02-24 RevE circuit board pic
2022-02-28 Moving heart rate board in
    [Mussel_heartrate_RevC.brd, Mussel_heartrate_RevC.sch]
2022-03-24 Changing cutoff voltage to 3.5
2022-03-25 Changing green flash timing
    Move the green flash to only happen once a minute when the Hall effect and temperature sensor are sampled. Starting battery test at 2 minute intervals.
2022-03-30 Change comments, battery cutoff voltage
2022-05-30 Remove extra comma at end of each file line
    We don't need a comma after the battery voltage since it's the last value on the line.
2022-05-31 Hall effect sensor board design
    [Hall_effect_sensor_A139x.kicad_sch, Hall_effect_sensor_board_A139x.kicad_pcb, Hall_effect_sensor_board_A139x.kicad_sch]
2022-05-31 Heart rate module RevC in KiCad
    [Mussel_heartrate_RevC.kicad_pcb, Mussel_heartrate_RevC.kicad_sch]
2022-05-31 Updated to KiCad 6.0.1
    [BivalveBit.kicad_pcb, BivalveBit.kicad_sch]
2022-12-02 Try this with a working board next
2022-12-02 Increase the wait time
    Syringe pump would miss triggers if the wait time between trigger events was less than 1500 milliseconds.
2023-01-05 Updated heart sensor to 200MA & 8T
2023-07-03 Creating code to use MAX3010x heart sensor - UNTESTED
2023-07-06 Functional test for MAX30102 - but use 5V supply
2023-07-10 Making this a bit more user-friendly, fail gracefully
    Should be functional for testing if the various sensors (gape sensor, VCNL4040, TMP117) and clock/SD are all functional.
